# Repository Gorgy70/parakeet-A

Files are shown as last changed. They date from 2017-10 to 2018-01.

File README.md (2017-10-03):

# parakeet-A

Перевод проекта Parakeet с платформы Wixel на платофрму Arduino.<br>
Данный проект основан на следующих проектах:<br>
1. Parakeet от Jamorham (https://jamorham.github.io, https://github.com/jamorham/wixel-xDrip)<br>
2. XDrip от Emma Black (http://stephenblackwasalreadytaken.github.io/xDrip, https://github.com/StephenBlackWasAlreadyTaken/xDrip)<br>
3. CC2500-Project от Don Browne (https://github.com/brownedon/CC2500-Project)<br>
<br>
<br>
<b>Сборка прибора:</b><br>
<br>
Для сборки прибора необходимы следующие компоненты:<br>
1. Контроллер Arduino Mini Pro ATmega328P 3.3V, 8MHz. Важно иметь именно такой контроллер. У котроллера на чипе ATmega168PA мало памяти, а контроллеры с напряжением 5V не будут работать.<br>
2. Радиомодуль на базе чипа Texas Instruments CC2500, желательно с усилителем слабого сигнала.<br>
Таких модулей не очень много в продаже, я их покупал на али у продавца e_goto Processors Store (https://www.aliexpress.com/store/1829717?spm=2114.13010608.0.0.rIN6UB).<br>
Были куплены и испытаны два модуля:<br>
https://www.aliexpress.com/item/Wireless-Module-CC2500-2-4G-Low-power-Consistency-Stability-Small-Size/32702148262.html?spm=2114.13010608.0.0.Y8KBPk<br>
Данный модуль без усилителя слабого сигнала обладает слабой чувствительностью и принимает сигнал на расстояниее не более 5 метров при отстутсвии препятсвий. Модуль не принимает сигнал через стену.<br>
https://www.aliexpress.com/item/CC2500-PA-LNA-2-4G-SPI-22dBm-Wireless-Data-Transceiver-Module/32606419424.html?spm=2114.13010608.0.0.X1eJmz<br>
Это модуль имеет усилитель слабого сигнала и очень неплохую чувствительность и рекомендуется к покупке.<br>
3. Модуль контроля заряда батареи.<br>
4. Аккумулятор 3.7 В.<br>
Я нашел аккумулятор под размер печатной платы:<br>
https://www.aliexpress.com/item/754060-MP3-MP4-2500MAH-3-7V-Bluetooth-stereo-mobile-power-polymer-lithium-battery/32790808657.html?spm=2114.13010608.0.0.TSSHRb
<br>
но можно использовать любой подходящий.<br>
5. Адаптер USB-Serial для заливки прошивки. Я покупал вот этот: http://robotdyn.ru/catalog/boards/usb_serial_adapter_ch340g_5v_3_3v/<br>
<br>
<br>
Соединяем между собой модули:<br>
VCC Радиомодуля - Контакт 3.3V Ардуино<br>
SCLK Радиомодуля - Контакт 13 Ардуино<br>
SI Радиомодуля - Контакт 11 Ардуино<br>
SO Радиомодуля - Контакт 12 Ардуино<br>
CSN Радиомодуля - Контакт 10 Ардуино<br>
GDO Радиомодуля - Контакт 9 Ардуино (может быть любым цифровым контактом. Назначается строкой #define GDO0_PIN в прошивке)<br>
GND Радиомодуля - Контакт GND Ардуино (земля)<br>
LEN Радиомодуля - Соединяется или с VCC Радиомодуля или контактом А1 Ардуино. Соединяется через сопротивление 10КОм. В случае подключения на контакт А1, необходимо компилировать скетч с ключом CC2500_LEN_CONTROL<br>
DTR GSM-Модема - Контакт 8 Ардуино (может быть любым цифровым контактом. Назначается строкой #define DTR_PIN в прошивке)<br>
RX GSM-Модема - Контакт 7 Ардуино (может быть любым цифровым контактом. Назначается строкой #define TX_PIN в прошивке)<br>
TX GSM-Модема - Контакт 6 Ардуино (может быть любым цифровым контактом. Назначается строкой #define RX_PIN в прошивке)<br>
GND GSM-Модема - На минус платы зарядки<br>
VCC GSM-Модема - На плюс платы зарядки<br>
Минус платы зарядки - Контакт GND Ардуино (земля)<br>
Контакт 5 Ардуино (может быть любым цифровым контактом. Назначается строкой #define YELLOW_LED_PIN в прошивке) - на желтый светодиод. Подключается последовательно с сопротивлением 100 Ом на землю.<br>
Контакт 4 Ардуино (может быть любым цифровым контактом. Назначается строкой #define RED_LED_PIN в прошивке) - на красный светодиод. Подключается последовательно с сопротивлением 100 Ом на землю.<br>
<br>
Для заливки прошивки в контроллер подключаем адаптер USB-Serial следующим образом:<br>
RX адаптера USB-Serial - RX Ардуино<br>
TX адаптера USB-Serial - TX Ардуино<br>
GND адаптера USB-Serial - GND Ардуино<br>
DTR адаптера USB-Serial - DTR Ардуино (можно подключить к контакту RST Ардуино через конденсатор в 1 мкФ<br>
Данная схема подключения подходит для моего адаптера USB-Serial. Для других может потребоваться другое подключение:br>
TX адаптера USB-Serial - RX Ардуино<br>
RX адаптера USB-Serial - TX Ардуино<br>
Правильная схема подключения адаптера выбирается экспериментально.<br>
<br>
В файле parakeet-A.lay6 находится печатная плата прибора в формате Sprint-Layout 6 (выражаю огромную благодарность Олегу Романовскому за помощь в разработке) <br>
К сожалению, в этой схеме не отражено подключение контакта LEN через сопротивление, а потому рекомендуется разорвать дорожку между контктами VCC и LEN радиомодуля и припаять сопротивление 10КОМ между контактом LEN радиомодуля и А1 Ардуины.<br>
В файле parakeet-A-v3.lay6 находится печатная плата, в которой добавлена дорожка для управлением усилителем слабого сигнала.<br>
В случае если вы строите прибор на основании этой платы вы должны переопределить контакт GDO0_PIN:<br>
#define GDO0_PIN A2            // Цифровой канал, к которму подключен контакт GD0 платы CC2500<br>
<br>
<b>Заливка прошивки в прибор:</b><br>
<br>
Для заливки прошивки необходимо установить Arduino IDE:<br>
https://www.arduino.cc/en/Main/Software
<br>
Открыть проект Parakeet-A, выбрать плату "Arduino Pro or Pro Mini", выбрать процессор "ATmega 328 (3.3V, 8MHz)", выбрать порт, скомпилировать и загрузить проект.<br>
В исходном тексте проекта можно вносить следующие изменения:<br>
ИД трансмиттера в строке<br>
char transmitter_id[] = "ABCDE";<br>
Так же ИД трансмиттера можно изменить с помощью СМС с текстом TRANSMIT <ИД трансмиттера><br>
APN вашего провайдера мобильной связи в строке<br>
#define my_gprs_apn   "internet.mts.ru"<br>
Этот параметр также можно изменить с помощью СМС с текстом APN <APN><br>
Цифровой код, который необходим для получения данных в программе xDrip. Цифровой код можно поменять в строке<br>
#define my_password_code  "12354"<br>
или с помощью СМС с текстом PWD <цифровой код>. Цифровой код должен состоять из 5 цифр.<br>
Адрес облачного сервиса. Адрес облачного сервиса, указанный в исходном коде прошивки является рабочим и абсолютно бесплатным, но вы можете указать свой собственный облачные сервис в строке<br>
#define my_webservice_url  "http://parakeet.esen.ru/receiver.cgi"<br>
или с помощью СМС с текстом HTTP <адрес облачного сервиса><br>

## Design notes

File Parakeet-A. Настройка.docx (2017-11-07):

Первоначальная настройка прибора Parakeet-A

1. Установка симкарты Симкарта должна быть формата микро и устанавливается чипом вверх и углом наружу.

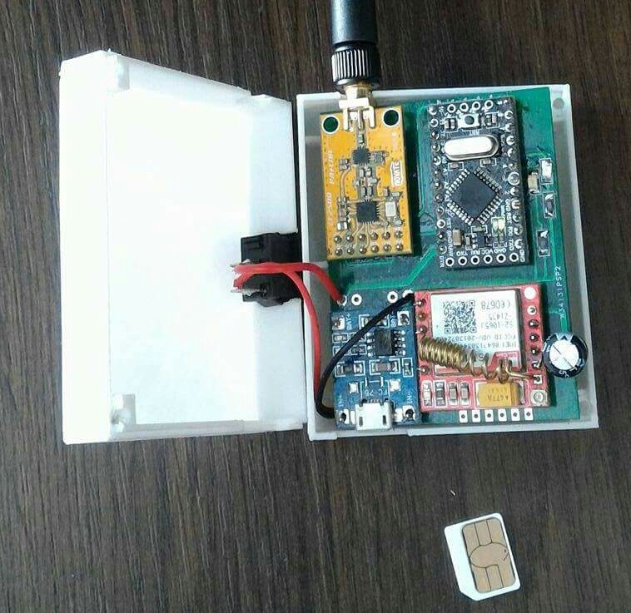
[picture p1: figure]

2. Включаем прибор и проверяем, что симкарта работает с модемом. Для проверки надо набрать номер симкарты.
3. Настраиваем параметры мобильного интернета вашего мобильного оператора. Необходимо отправить СМС с текстом APN <apn вашего мобильного оператора>. Для МТС текст данного смс будет APN internet.mts.ru, для Билайн: APN internet.beeline.ru и т.д. При успешной обработке данного СМС мы должны получить ответное смс с текстом APN: <apn вашего провайдера>.
4. Настраиваем код трансмиттера Dexcom. Необходимо отправить СМС с текстом TRANSMIT <код трансмиттера>. При успешной обработке данного СМС мы должны получить ответное смс с текстом TRANSMIT: < код трансмиттера >.
5. Скачиваем приложение для мобильного телефона xDrip+ с сайта разработчика https://github.com/StephenBlackWasAlreadyTaken/xDrip/wiki/Download-Current-Version.
6. Устанавливаем данное приложение на мобильный телефон с андроид.
7. Настраиваем источник данных в программе xDrip+. Меню – Настройки – Источник данных – выбрать WiFi Wixel / Parakeet:

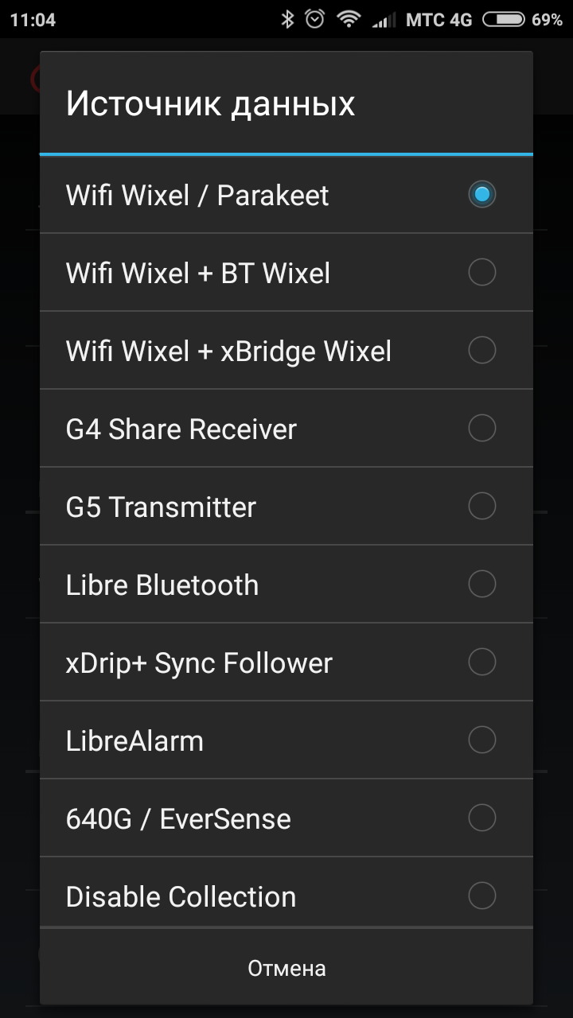
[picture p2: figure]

8. Настраиваем адрес облачного сервиса в программе xDrip+. Меню – Настройки – Список приемников. В форме ввода введите http://parakeet.esen.ru/<код (http://parakeet.esen.ru/%3cкод) трансмиттера>/12354/json.get

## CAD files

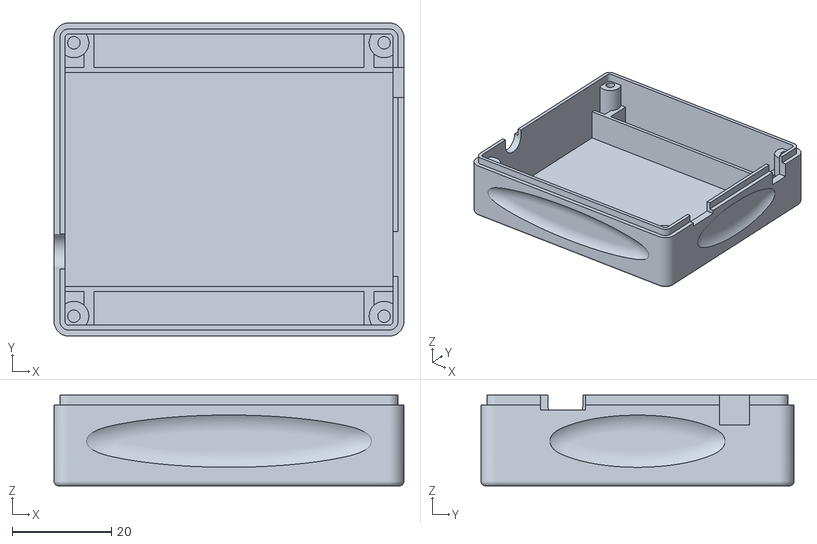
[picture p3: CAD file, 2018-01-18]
CaseBottom5.stl
70.4 x 63.0 x 18.3

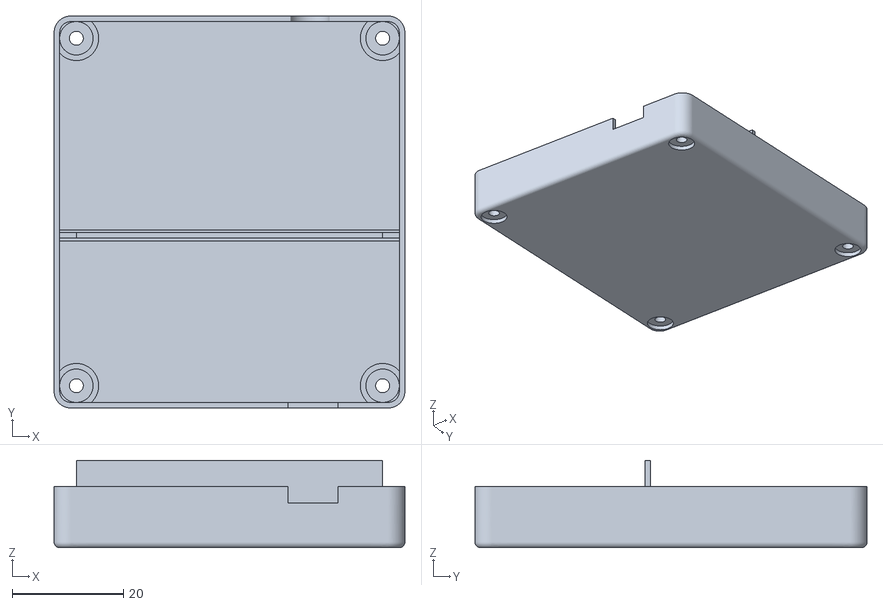
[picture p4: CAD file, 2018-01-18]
CaseTop4.stl
63.0 x 70.4 x 15.7

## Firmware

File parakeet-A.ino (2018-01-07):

#define NEW_PCB
#define NEW_PCB_V3
//#define DEBUG
#define GSM_MODEM
#define ARDUINO_SLEEP
//#define ARDUINO_DELAY
//#define INT_BLINK_LED
#define EXT_BLINK_LED
#define MODEM_SLEEP_DTR
#define CC2500_LEN_CONTROL
//#define NO_NEXT_TIME // Не пытаемся угадать время следующего пакета

#include <SPI.h>
#include <SoftwareSerial.h>
#include <EEPROM.h>
#include "cc2500_REG.h"

#ifdef ARDUINO_SLEEP
#include <avr/sleep.h>     //AVR MCU power management.
#include <avr/power.h>     //AVR MCU peripheries (Analog comparator, ADC, USI, Timers/Counters etc) management.
#include <avr/wdt.h>       //AVR MCU watchdog timer management.
#include <avr/io.h>        //AVR MCU IO ports management.
#include <avr/interrupt.h> //AVR MCU interrupt flags management.
#endif

#ifdef NEW_PCB
#ifdef NEW_PCB_V3
  #define GDO0_PIN A2           // Цифровой канал, к которму подключен контакт GD0 платы CC2500
#else
  #define GDO0_PIN 9            // Цифровой канал, к которму подключен контакт GD0 платы CC2500
#endif
  #define DTR_PIN  8            // Цифровой канал, к которму подключен контакт DTR платы GSM-модема
  #define TX_PIN   7            // Tx контакт для последовательного порта
  #define RX_PIN   6            // Rx контакт для последовательного порта
  #define RED_LED_PIN 4
  #define YELLOW_LED_PIN 5
#else
  #define GDO0_PIN 3            // Цифровой канал, к которму подключен контакт GD0 платы CC2500
  #define DTR_PIN  2            // Цифровой канал, к которму подключен контакт DTR платы GSM-модема
  #define TX_PIN   8            // Tx контакт для последовательного порта
  #define RX_PIN   9            // Rx контакт для последовательного порта

  #ifdef EXT_BLINK_LED
    #define RED_LED_PIN 5
    #define YELLOW_LED_PIN 4
  #endif
#endif
#define LEN_PIN    A1            // Цифровой канал, к которму подключен контакт LEN (усилитель слабого сигнала) платы CC2500


#define NUM_CHANNELS (4)      // Кол-во проверяемых каналов
#define FIVE_MINUTE 300000    // 5 минут

#ifdef DEBUG
#define SERIAL_BUUFER_LEN 110 // Размер буфера для приема данных от GSM модема
#else
#define SERIAL_BUUFER_LEN 200 // Размер буфера для приема данных от GSM модема
#endif
#define GSM_BUUFER_LEN 200 // Размер буфера для приема данных от GSM модема

#define GSM_DELAY 200         // Задержка между командами модема

#define my_webservice_url  "http://parakeet.esen.ru/receiver.cgi"
#define my_webservice_reply     "!ACK"
#define my_user_agent     "parakeet_A"
#define my_gprs_apn   "internet.mts.ru"
//#define my_gprs_apn   "internet.beeline.ru"
//#define my_gprs_apn   "vmi.velcom.by"
#define my_password_code  "12354"
#define WDTO_2S_MS 2371 // Время ожидания строжевого пса "примерно 2 секунды"
#define ERROR_STR "ERROR" // Сообщение об ошибке при работе с модемом

SoftwareSerial mySerial(RX_PIN, TX_PIN); // RX, TX

unsigned long dex_tx_id;
char transmitter_id[] = "ABCDE";
//char transmitter_id[] = "6518Y";
//char transmitter_id[] = "69NL1";
//char transmitter_id[] = "619MY";
//char transmitter_id[] = "62SAL";
//char transmitter_id[] = "607K5";

unsigned long packet_received = 0;

//byte fOffset[NUM_CHANNELS] = { 0x00, 0xD5, 0xE6, 0xE5 };
//byte defaultfOffset[NUM_CHANNELS] = { 0x00, 0xD5, 0xE6, 0xE5 };
//byte fOffset[NUM_CHANNELS] = { 0xCE, 0xD5, 0xE6, 0xE5 };
byte fOffset[NUM_CHANNELS] = { 0xE4, 0xE3, 0xE2, 0xE2 };
//byte defaultfOffset[NUM_CHANNELS] = { 0xCE, 0xD5, 0xE6, 0xE5 };
byte nChannels[NUM_CHANNELS] = { 0, 100, 199, 209 };
//unsigned long waitTimes[NUM_CHANNELS] = { 13500, 500, 500, 500 };
//unsigned long waitTimes[NUM_CHANNELS] = { 0, 500, 500, 500 };
unsigned long waitTimes[NUM_CHANNELS] = { 0, 600, 600, 600 };
//unsigned long catch_offsets[NUM_CHANNELS] = { 0, 0, 0, 0 };

byte sequential_missed_packets = 0;
byte wait_after_time = 100;
unsigned long next_time = 0; // Время ожидания следующего пакета на канале 0
unsigned long catch_time = 0; // Время последнего пойманного пакета (приведенное к пакету на канале 0)

byte misses_until_failure = 2;                                                   //
// after how many missed packets should we just start a nonstop scan?                               //
// a high value is better for conserving batter life if you go out of wixel range a lot             //
// but it could also mean missing packets for MUCH longer periods of time                           //
// a value of zero is best if you dont care at all about battery life                               //

boolean gsm_availible = false; // Доступность связи GSM
boolean modem_availible = false; // Доступность модема на порту
boolean internet_availible = false; // Флаг подключения мобильного интернета
char SerialBuffer[SERIAL_BUUFER_LEN] ; // Буффер для чтения данных их последовательного порта
char gsm_cmd[GSM_BUUFER_LEN]; // Буффер для формирования GSM команд
boolean low_battery = false;
byte gsm_error_count = 0;

#ifdef ARDUINO_SLEEP
volatile long watchdog_counter;
int wdto_2s_ms = WDTO_2S_MS;
#endif

// Коды ошибок мигают лампочкой в двоичной системе
// 1 (0001) - Неверный CRC в сохраненных настройках. Берем настройки по умолчанию
// 2 (0010) - Не подключен модем.
// 3 (0011) - Нет мобильной связи
// 4 (0100) - Нет мобильного интернета
// 

typedef struct _Dexcom_packet
{
  byte len;
  unsigned long dest_addr;
  unsigned long src_addr;
  byte port;
  byte device_info;
  byte txId;
  unsigned int raw;
  unsigned int filtered;
  byte battery;
  byte unknown;
  byte checksum;
  byte RSSI;
  byte LQI2;
} Dexcom_packet;

Dexcom_packet Pkt;

typedef struct _parakeet_settings
{
  unsigned long dex_tx_id;     //4 bytes
  char http_url[56];
  char gsm_apn[32];
  char password_code[6];
  unsigned long checksum; // needs to be aligned

} parakeet_settings;

parakeet_settings settings;

char SrcNameTable[32] = { '0', '1', '2', '3', '4', '5', '6', '7',
                          '8', '9', 'A', 'B', 'C', 'D', 'E', 'F',
                          'G', 'H', 'J', 'K', 'L', 'M', 'N', 'P',
                          'Q', 'R', 'S', 'T', 'U', 'W', 'X', 'Y'
                        };


void dexcom_src_to_ascii(unsigned long src, char addr[6]) {
  addr[0] = SrcNameTable[(src >> 20) & 0x1F];
  addr[1] = SrcNameTable[(src >> 15) & 0x1F];
  addr[2] = SrcNameTable[(src >> 10) & 0x1F];
  addr[3] = SrcNameTable[(src >> 5) & 0x1F];
  addr[4] = SrcNameTable[(src >> 0) & 0x1F];
  addr[5] = 0;
}


unsigned long getSrcValue(char srcVal) {
  byte i = 0;
  for (i = 0; i < 32; i++) {
    if (SrcNameTable[i] == srcVal) break;
  }
  return i & 0xFF;
}

unsigned long asciiToDexcomSrc(char addr[6]) {
  unsigned long src = 0;
  src |= (getSrcValue(addr[0]) << 20);
  src |= (getSrcValue(addr[1]) << 15);
  src |= (getSrcValue(addr[2]) << 10);
  src |= (getSrcValue(addr[3]) << 5);
  src |= getSrcValue(addr[4]);
  return src;
}

byte bit_reverse_byte (byte in)
{
    byte bRet = 0;
    if (in & 0x01)
        bRet |= 0x80;
    if (in & 0x02)
        bRet |= 0x40;
    if (in & 0x04)
        bRet |= 0x20;
    if (in & 0x08)
        bRet |= 0x10;
    if (in & 0x10)
        bRet |= 0x08;
    if (in & 0x20)
        bRet |= 0x04;
    if (in & 0x40)
        bRet |= 0x02;
    if (in & 0x80)
        bRet |= 0x01;
    return bRet;
}

void bit_reverse_bytes (byte * buf, byte nLen)
{
    byte i = 0;
    for (; i < nLen; i++)
    {
        buf[i] = bit_reverse_byte (buf[i]);
    }
}

unsigned long dex_num_decoder (unsigned int usShortFloat)
{
    unsigned int usReversed = usShortFloat;
    byte usExponent = 0;
    unsigned long usMantissa = 0;
    bit_reverse_bytes ((byte *) & usReversed, 2);
    usExponent = ((usReversed & 0xE000) >> 13);
    usMantissa = (usReversed & 0x1FFF);
    return usMantissa << usExponent;
}

#ifdef EXT_BLINK_LED
void blink_sequence_red(const char *sequence) {
  byte i;

  digitalWrite(YELLOW_LED_PIN, HIGH);
  digitalWrite(RED_LED_PIN, LOW);
  delay(500); 
  for (i = 0; i < strlen(sequence); i++) {
    digitalWrite(RED_LED_PIN, HIGH);
    switch (sequence[i]) {
      case '0': 
        delay(500);
        break;
      case '1': 
        delay(1000);
        break;
      default:
        delay(2000);
        break;
    }
    digitalWrite(RED_LED_PIN, LOW);
    delay(500); 
  }  
  digitalWrite(YELLOW_LED_PIN, LOW);
}
#endif

#ifdef INT_BLINK_LED
void blink_sequence(const char *sequence) {
  byte i;

  digitalWrite(LED_BUILTIN, LOW);
  delay(500); 
  for (i = 0; i < strlen(sequence); i++) {
    digitalWrite(LED_BUILTIN, HIGH);
    switch (sequence[i]) {
      case '0': 
        delay(500);
        break;
      case '1': 
        delay(1000);
        break;
      default:
        delay(2000);
        break;
    }
    digitalWrite(LED_BUILTIN, LOW);
    delay(500); 
  }  
}
#endif

void clearSettings()
{
  memset (&settings, 0, sizeof (settings));
  settings.dex_tx_id = asciiToDexcomSrc (transmitter_id);
  dex_tx_id = settings.dex_tx_id;
  sprintf(settings.http_url, my_webservice_url);
  sprintf(settings.gsm_apn, my_gprs_apn);
  sprintf(settings.password_code, my_password_code);
}

unsigned long checksum_settings()
{
  char* flash_pointer;
  unsigned long chk = 0x12345678;
  byte i;
  //   flash_pointer = (char*)settings;
  flash_pointer = (char*)&settings;
  for (i = 0; i < sizeof(parakeet_settings) - 4; i++)
  {
    chk += (flash_pointer[i] * (i + 1));
    chk++;
  }
  return chk;
}

void saveSettingsToFlash()
{
  settings.checksum = checksum_settings();
  EEPROM.put(0, settings);
}

void loadSettingsFromFlash()
{
  EEPROM.get(0, settings);
  dex_tx_id = settings.dex_tx_id;
  if (settings.checksum != checksum_settings()) {
#ifdef DEBUG
    Serial.println("Settings checksum error. Load defaults");
#endif
    clearSettings();
#ifdef INT_BLINK_LED
    blink_sequence("0001");
#endif
#ifdef EXT_BLINK_LED
    blink_sequence_red("0001");
#endif
  }
#ifdef DEBUG
  Serial.print("Dexcom ID: ");
  Serial.println(settings.dex_tx_id);
#endif
}

#ifdef INT_BLINK_LED
void blink_builtin_led_quarter() {  // Blink quarter seconds
  if ((millis() / 250) % 2) {
    digitalWrite(LED_BUILTIN, HIGH);
  } else
  {
    digitalWrite(LED_BUILTIN, LOW);
  }
}

void blink_builtin_led_half() {  // Blink half seconds
  if ((millis() / 500) % 2) {
    digitalWrite(LED_BUILTIN, HIGH);
  } else
  {
    digitalWrite(LED_BUILTIN, LOW);
  }
}
#endif

#ifdef EXT_BLINK_LED
void blink_yellow_led_quarter() {  // Blink quarter seconds
  if ((millis() / 250) % 2) {
    digitalWrite(YELLOW_LED_PIN, HIGH);
  } else
  {
    digitalWrite(YELLOW_LED_PIN, LOW);
  }
}

void blink_yellow_led_half() {  // Blink half seconds
  if ((millis() / 500) % 2) {
    digitalWrite(YELLOW_LED_PIN, HIGH);
  } else
  {
    digitalWrite(YELLOW_LED_PIN, LOW);
  }
}

void blink_red_led_quarter() {  // Blink quarter seconds
  if ((millis() / 250) % 2) {
    digitalWrite(RED_LED_PIN, HIGH);
  } else
  {
    digitalWrite(RED_LED_PIN, LOW);
  }
}

void blink_red_led_quarter2() {  // Blink quarter seconds
  if ((millis() / 250) % 2) {
    digitalWrite(RED_LED_PIN, LOW);
  } else
  {
    digitalWrite(RED_LED_PIN, HIGH);
  }
}

void blink_red_led_half() {  // Blink half seconds
  if ((millis() / 500) % 2) {
    digitalWrite(RED_LED_PIN, HIGH);
  } else
  {
    digitalWrite(RED_LED_PIN, LOW);
  }
}

void blink_red_led_half2() {  // Blink half seconds
  if ((millis() / 500) % 2) {
    digitalWrite(RED_LED_PIN, LOW);
  } else
  {
    digitalWrite(RED_LED_PIN, HIGH);
  }
}
#endif

void WriteReg(char addr, char value) {
  digitalWrite(SS, LOW);
  while (digitalRead(MISO) == HIGH) {
  };
  SPI.transfer(addr);
  SPI.transfer(value);
  digitalWrite(SS, HIGH);
  //  delay(10);
}

char SendStrobe(char strobe)
{
  digitalWrite(SS, LOW);

  while (digitalRead(MISO) == HIGH) {
  };

  char result =  SPI.transfer(strobe);
  digitalWrite(SS, HIGH);
  //  delay(10);
  return result;
}
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

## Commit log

2016-11-16 Найдены правильные значения регистров для чипа CC2500
2016-11-18 Установил копию с рабочего компа
2016-11-21 1. Разработан алгоритм приема пакетов от трансмиттера 2. Чтение настроек из ЕПРОМа
2016-11-22 Добавлены отладочные сообщения. Увеличено время ожидания пакета на канале 0 Отсчет времени следующего пакета ведется от времени пройманного пакета Добавлена обработка переполнения счетчика времени. В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
2016-12-03 Исправленый алгоритмы ожидания пакета Приемник включается за 2 секунды до времени ожидания пакета
2016-12-03 Добавлено преобразование значений уровня глюкозы
2016-12-03 Подправлены интервалы ожидания
2016-12-13 Добавлена работа с GSM модемом. Без разбора пришедших СМС
2016-12-14 Небольшие исправления
2016-12-20 Добавлен код для работа с GSM модемом Добавлена визуализация ошибок миганием
2016-12-22 Добавлен разбор входящих СМС Добавлен ответ на входящие СМС Сделаны паузы между командами модема
2016-12-23 Небольшие исправления и добавление отладочного вывода
2016-12-24 Первая рабочая версия программы
2017-01-19 Изменены контакты GDO0_PIN,RX_PIN,TX_PIN для удобства пайки Небольшие исправления
2017-02-01 1. Альтернативные параметры радиомодуля 2. Обработка регистра REQUEST радиомодуля
2017-02-02 В альтернативной настройке радиорегистров исправлен регистр IOCFG0 Добавлен на вскяий случай текущий трансмиттер Альтернативная настройка радиорегистров показала отличные результаты
2017-02-06 Приложение исправлено для платы Mini Pro Мигание вынесено под ключ компиляции Для модема в режиме ожидания отключается мигание и включается режим сна.
2017-02-07 Добавлена процедура побудки модема. Данная процедура добавлена в процедуру отправки данных в облако.
2017-02-10 Убран буфер в локальной процедуре чтения пакета декском
2017-03-02 Добавлен текст в Read.me Добавлен алгоритм сна вместо delay Удален старый вариант настроек радиомодуля
2017-03-02 Исправлена ошибка форматирования
2017-03-02 Исправлены орфографические ошибки
2017-03-02 Форматирование текста
2017-03-03 Доработано код режима сна
2017-03-05 Исправление ошибок в режиме сна
2017-03-08 Отладка режима сна. Небольшое изменение алгоритма приема пакетов Декскома
2017-03-19 Исправлена ощибка с ключами компиляции Добавлена работа с внешнеми светодиодами Исправлен алгоритм спящего режима
2017-03-20 Добавлен текст в описание
2017-03-22 Убрано заполнение регистра REQUEST Добавлена сигнализация о низком заряде батареи Окорректирован спящий режим
2017-03-22 Исправлена ошибка индикации низкого заряда батареи
2017-03-23 Подправлена работа световой индикации
2017-03-24 Исправлена работа с СМС сообщениями.
2017-04-05 Оптимизирован спящий режим контроллера
2017-04-06 Добавлена калибровка строжевого пса
2017-04-12 Исправлена ошибка в печатной плате
2017-04-22 После двух неудачных попыток отправить данные в облако, будет произведена полная инициализация модема
2017-05-16 Небольшие исправления логики работы с модемом. На плате в контактах для программирования увеличены интервалы.
2017-06-07 Добавлена дорожка на RST модема Внесены исправления в алгоритм инициализации модема в случае потери связи.
2017-06-08 Очередные исправления в случае неудачного GSM соединения
2017-09-06 Исправлена ошибка при обработке СМС SETTINGS
2017-09-08 Версия из гитхаба
2017-09-08 Добавлено управление усилителем слабого сигнала
2017-09-11 Довлен код управления усилителем слабого сигнала радиомодуля
2017-09-20 Управление усилителем слабого сигнала теперь и в базовой версии. Исправлено описание схемы соединения
2017-10-02 Исправлена процедура отправки СМС Добавлен сброс счетчика пропущеных пакетов при успешном приеме
2017-10-02 Добавлен корпус прибора Добавлена печатная плата с дорожкой управления усилителем слабого сигнала Добавлена информация в readme.
    [CaseBottom2.stl, CaseTop2.stl]
2017-10-03 Обновлено с сети
    [CaseBottom2.stl, CaseTop2.stl]
2017-10-19 Добавлена обработка сообщения ERROR при работе с модемом
2017-10-27 Исправлена ошибка обработки сообщения ERROR модема
2017-11-07 Подправлены режимы ожидания пакета
2017-11-07 Добавлено описание настройки прибора
2017-12-22 Изменена процедура мигания ошибки
2018-01-07 Исправлена ощибка обработки СМС APN
2018-01-18 New PCB New Case
    [CaseBottom2.stl, CaseBottom5.stl, CaseTop2.stl, CaseTop4.stl]
